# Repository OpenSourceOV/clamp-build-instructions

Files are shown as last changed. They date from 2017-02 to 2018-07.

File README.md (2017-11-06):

# Clamp Build Instructions

There are two versions of the clamp:

* [Version 2](./version-2.md) (RECOMMENDED) - complete re-design that integrates a hand lens (loupe) for magnification. This is the preferred version because of the flexibility to attach any magnification hand lens (conceivably 40x, but untested). 20x magnification is the minimum magnification for most stems.

* [Version 1](./version-1.md) - the original which uses a [Moment](https://www.shopmoment.com/) smartphone macro lens and has a magnification limit of 10x. Build instructions for Version 1 are here: [version-1.md](./version-1.md)

All clamp versions require a separate circuit to provide power and interface the Raspberry Pi with the LEDs. There are two versions. Version 1 which integrates the components on a PCB and version 2 where the components are connected inline without a PCB. Version 2 is strongly recommended unless you want to integrate other sensors, in which case Version 1 would be more useful. If you are planning to use Version 1 then you should enclose the circuit in a case.

* [Version 2](./switching-circuit-2.md) (RECOMMENDED) - inline version. Build instructions for Version 2 are here: [switching-circuit-2.md](./switching-circuit-2.md)

* [Version 1](./switching-circuit-1.md) - uses a PCB to mount the components. Build instructions for Version 1 are here: [switching-circuit-1.md](./switching-circuit-1.md)

A guide for wiring connectors is also provided:

* [Wiring Connectors](./wiring-connectors.md)

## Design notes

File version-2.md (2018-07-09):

# Clamp Version 2 Assembly Guide

## Schema

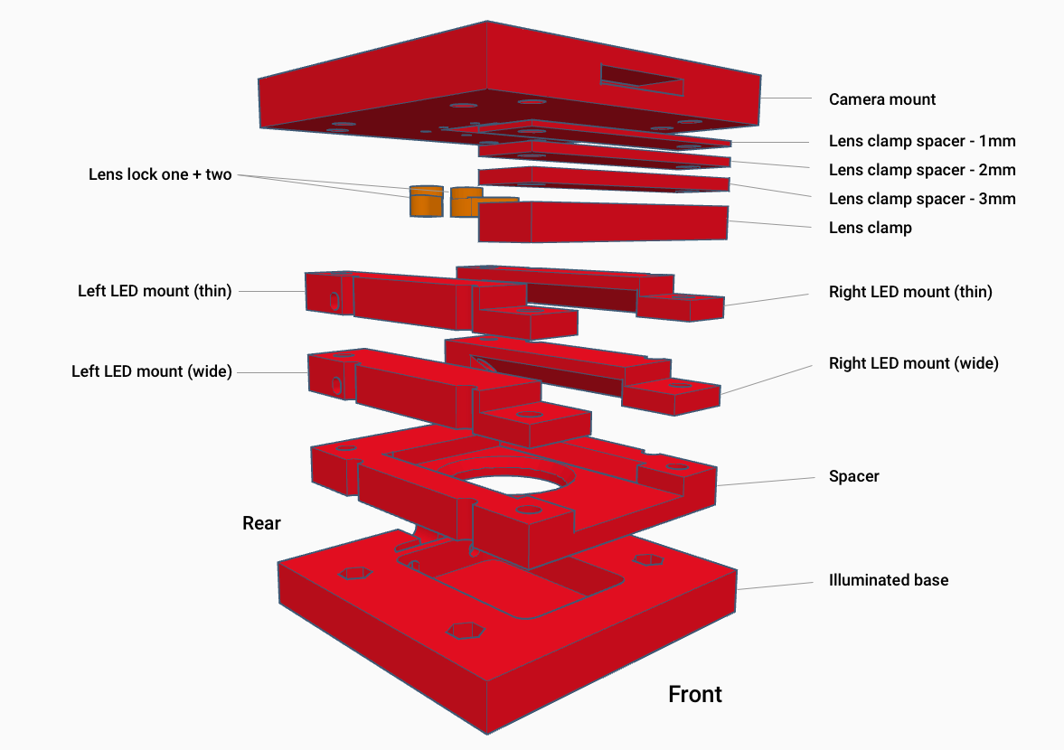
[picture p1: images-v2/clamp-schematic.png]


* **Camera mount** - to mount the camera and bolt the assembly together to the base
* **Lens clamp spacers** - used to increase the space between the top of the hand lens case and the bottom of the camera mount. Most hand lenses have a screw that sits proud and attaches the lens to the case. Without an appropriate spacer the hand lens sits at an angle. Only one need be used.
* **LED mounts** - to mount the LED strips. A wider mount to be used with most hand lenses and thinner mounts if more space is needed for a wider hand lens. Only one mount set is used (thin or wide).
* **Lens lock** - to hold the lens in place. Most lenses are firmly fixed to the case and don't move so these are normally not required.
* **Spacer** - to keep the sample in place and set the distance between hand lens and sample.
* **Illuminated base** - to provide the source of transmitted light and base for bolting the assembly together (diffuser layer not shown, more details below)

## Parts

Quantity | Part | Additional information
---------|------|---------
1|3D-printed clamp parts|Models and more information available in the [Clamp 3D Printing Resources](https://github.com/OpenSourceOV/clamp-3d-printing-resources) repository (**version 2** parts required).
6|50mm Superbright LED light strip sections|For the LED mounts and illuminated base. Usually come in long strips that can be cut into smaller sections. Typically used for accent lighting in kitchens etc. Can be purchased online from a number of places - these are some from Jaycar - [Ultra Bright IP67 Waterproof LED Flexible Strip Light](https://www.jaycar.com.au/ultra-bright-ip67-waterproof-led-flexible-strip-light/p/ZD0579). Note **50mm** sections are required.
1|Raspberry Pi Camera v2 module| See RaspberryPi.org for [more information](https://www.raspberrypi.org/products/camera-module-v2/) and list of suppliers
1|Rasberry Pi Camera long cable| Although the Camera comes with a short cable, a long cable makes life much easier. Most Raspberry Pi suppliers should stock longer cables e.g. [Little Bird Electronics - Flex Cable for Raspberry Pi Camera - 18 / 457mm](https://littlebirdelectronics.com.au/collections/raspberry-pi-cables-headers/products/flex-cable-for-raspberry-pi-camera-18-457mm)
1|Hand lens (loupe)|10-20 magnification e.g. Eschenbach 20x achromatic hand lens is excellent.
6|100mm lengths 25 AWG hookup cable (red)| For the LED mounts and illuminated base.
6|100mm lengths 25 AWG hookup cable (black)| For the LED mounts and illuminated base.
1|Sample pot of white acrylic paint| For the illuminated base.
1|Small paintbrush| For the illuminated base.
1|8mm x 90mm x 90mm (w x l x h) acrylic light diffuser (opaque plastic)|For the illuminated base.
4|5mm x ~70mm mushroom (or other) head bolts| For the illuminated base.
4|5mm x ~60mm hex head bolts| For the top assembly.
16+|5mm nuts| For the top assembly.
20+|5mm washers| For the top assembly.
4|2.5mm x 8mm screws (flat head)| For the camera mount.
4|2.5mm nuts| For the camera mount.
6|3mm nuts| For the lens locks.
2|3mm washers| For the lens locks.
2|~35mm x 3mm bolts| For the lens locks.
3|4-pin mini molex connector sets (each set containing a male and female connector)|e.g. [Jaycar - 4 Pin Mini Molex Plug/Socket](https://www.jaycar.com.au/4-pin-mini-molex-plug-socket/p/PP2027) or [Sparkfun - JST RCY Connector - Male/Female Set (2-pin)](https://www.sparkfun.com/products/10501) (but using extra to make up the connections required). For the LED mounts and illuminated base.

## Tools

Tool|Additional info|
---|-----
Soldering iron|
Solder|
Wire cutters| Flush / Diagonal cutters are particularly good e.g. [Spark fun - Flush Cutters](https://www.sparkfun.com/products/11952)
Small needle-nose pliers| e.g. [Spark fun - Needle Nose Pliers](https://www.sparkfun.com/products/8793)
Voltmeter/Multimeter| 
Third hand tool| e.g. [Spark fun - Third Hand](https://www.sparkfun.com/products/9317)

## Instructions

1. Paint the light well of the illuminated base white and leave to dry.

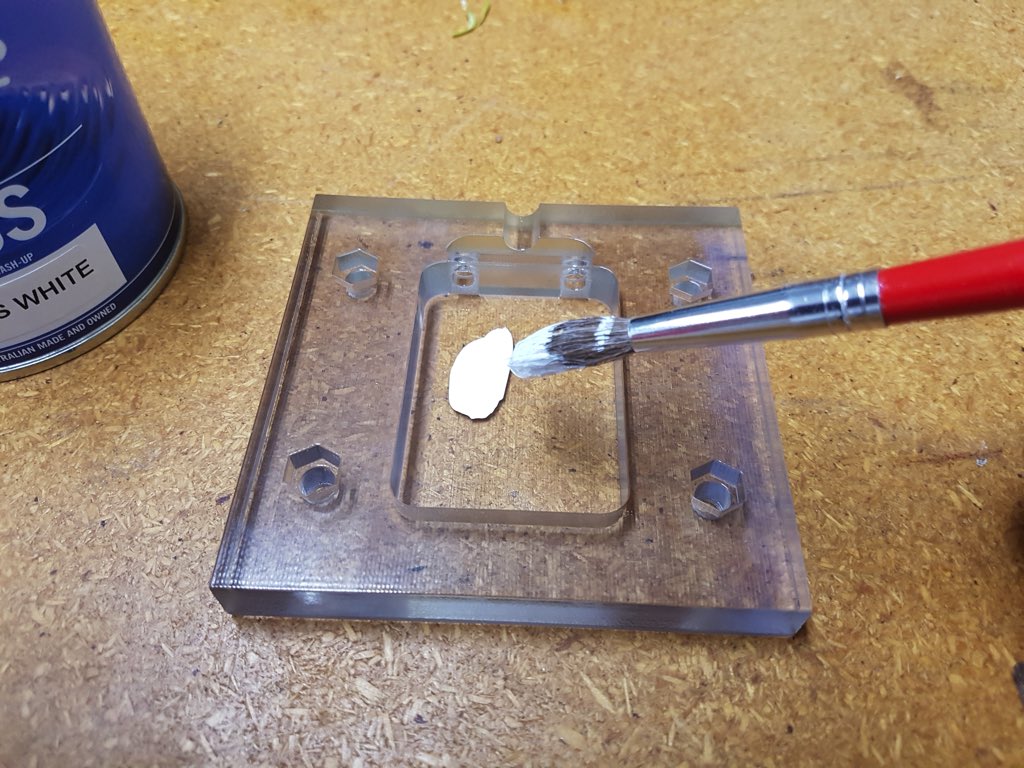
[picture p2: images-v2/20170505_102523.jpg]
    
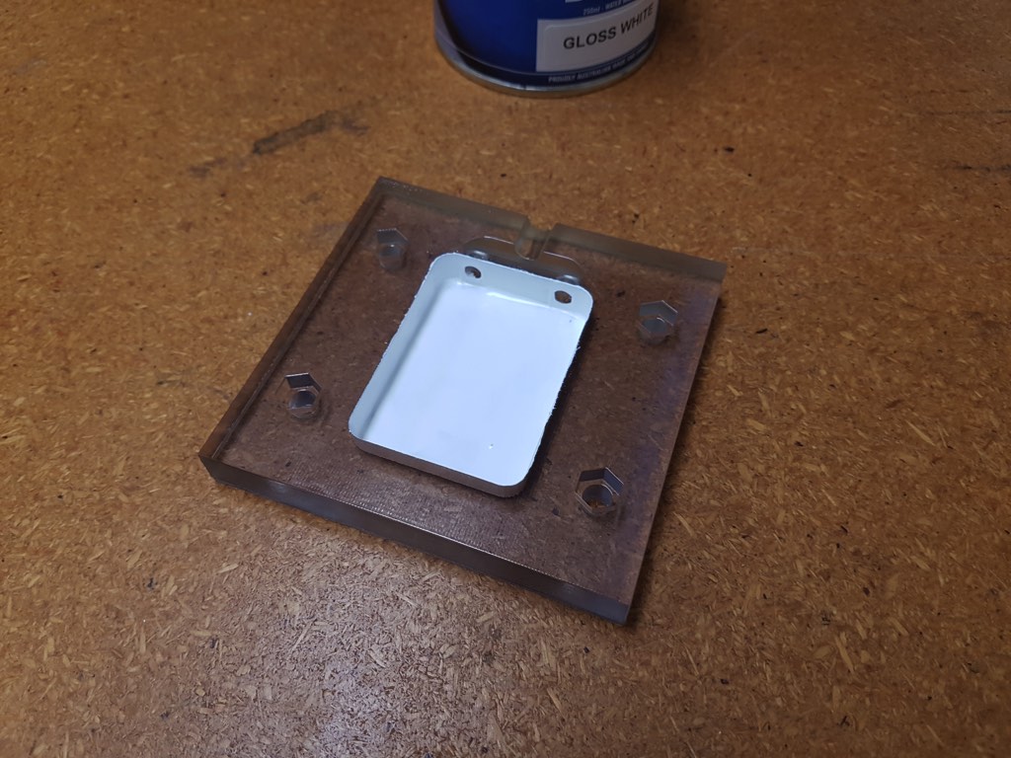
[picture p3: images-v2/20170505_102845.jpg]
    

2. Solder 100mm lengths of 25 AWG red and black wires to the positive and negative terminals of one side of each 2 50mm light strips.

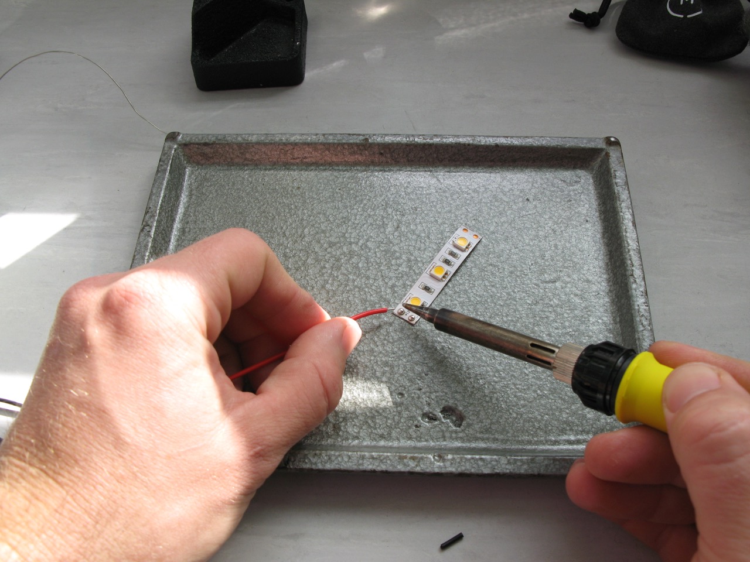
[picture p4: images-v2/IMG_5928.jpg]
    

3. Feed the wires through the holes at one end of the illuminated base, remove the adhesive backing labels and stick the LED strip sections in place as shown.

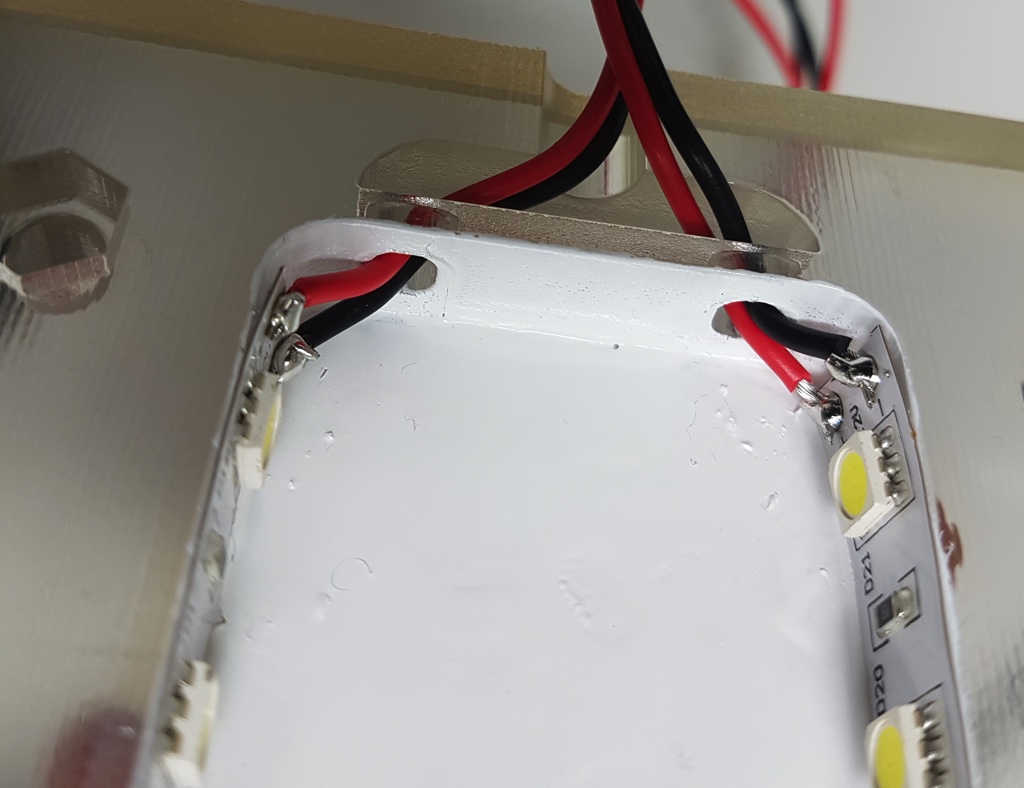
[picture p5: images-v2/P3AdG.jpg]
    

4. Insert a 5mm nut in a nut recess in the illuminated base, turn over and screw through a 5mm x ~80mm bolt. Repeat for the other 3 recesses.

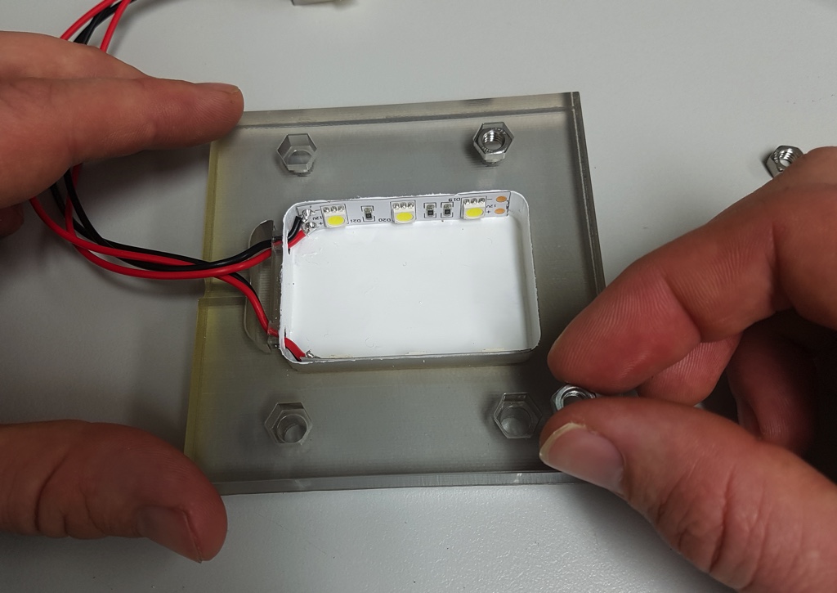
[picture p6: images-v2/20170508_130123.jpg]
    
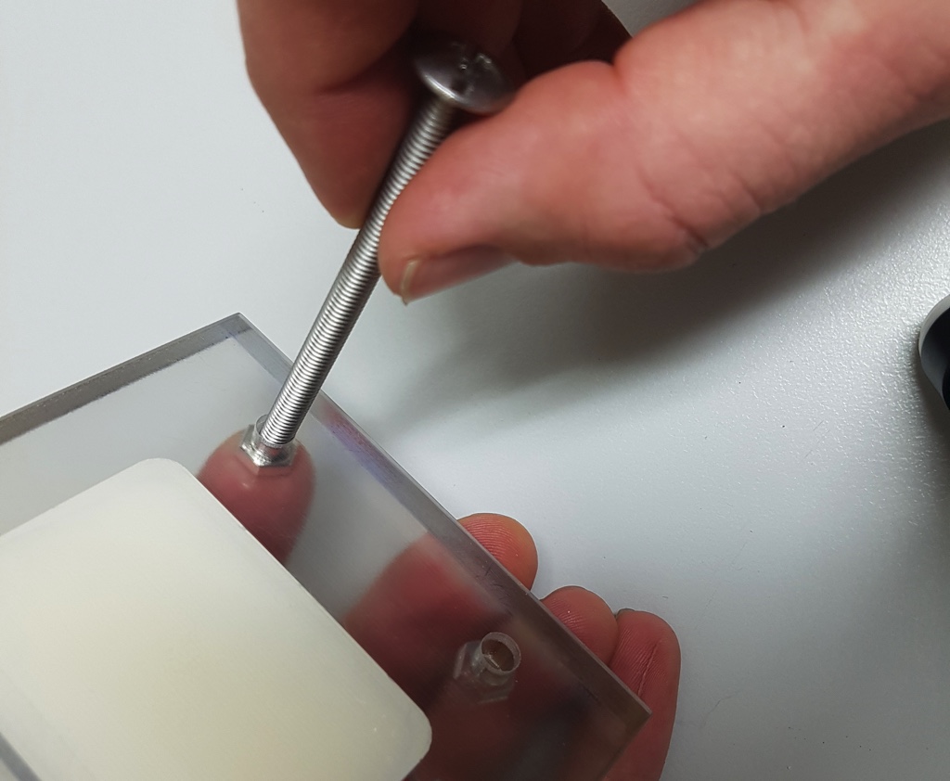
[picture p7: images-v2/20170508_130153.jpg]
    
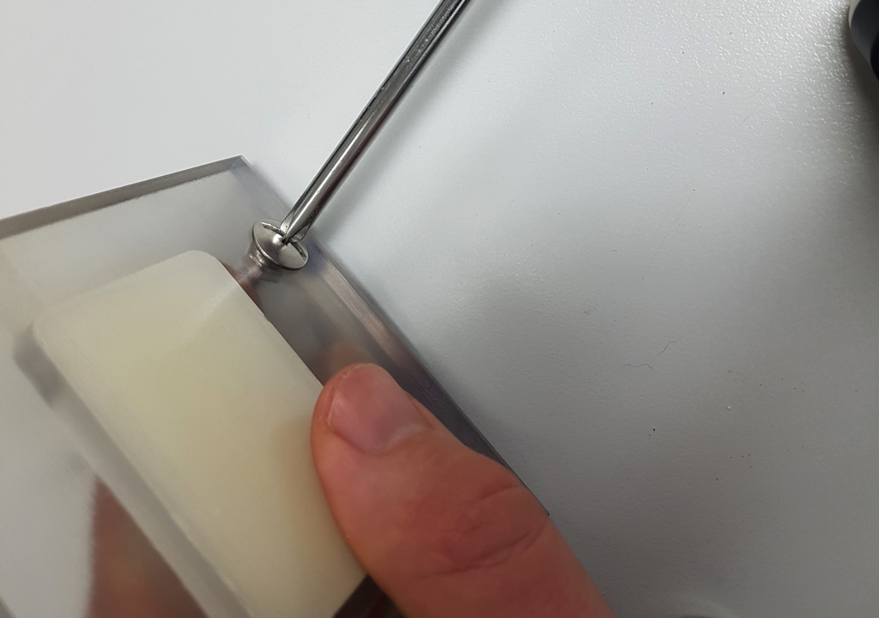
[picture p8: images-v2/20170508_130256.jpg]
    

5. Drill four holes in the diffuser and insert over the illuminator bolts. Tip: to mark where to drill the holes in the diffuser, align and hold the diffuser against the 3D printed foot then put it up against a light so you can see the holes shine through the diffuser plastic. Mark the centre of each hole with a marker then remove the diffuser, place on a flat piece of scrap wood and carefully drill through the diffuser into the wood. Gently is the key - acrylic sheets when drilled can easily shatter and crack.

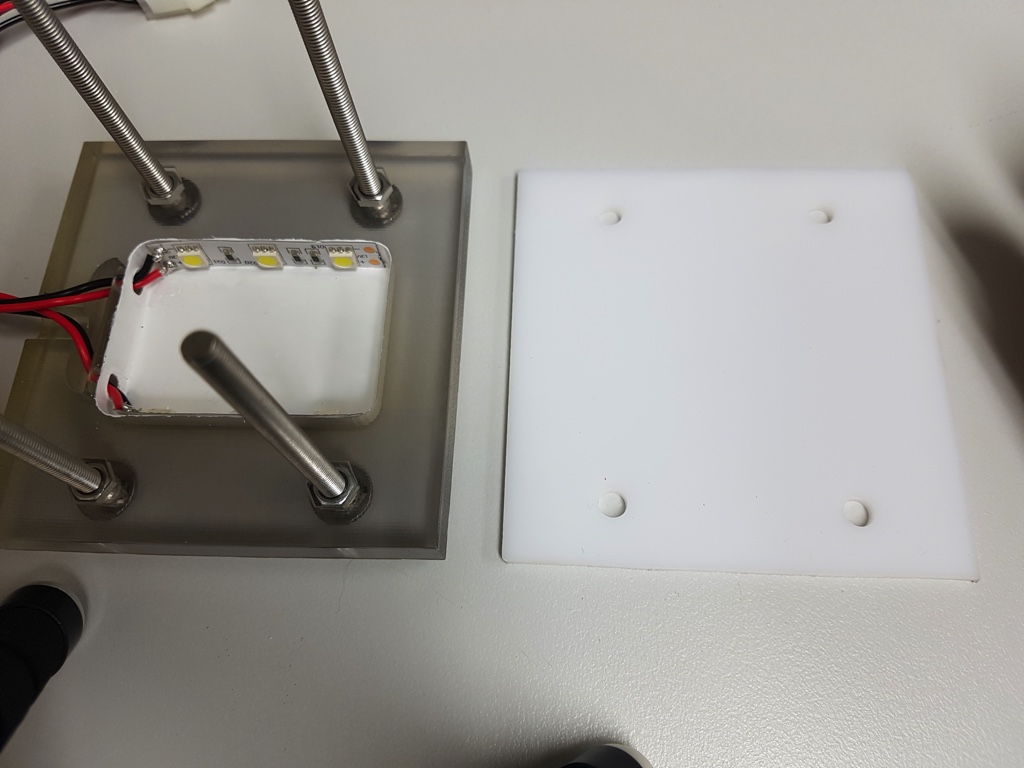
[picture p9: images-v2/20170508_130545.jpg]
    
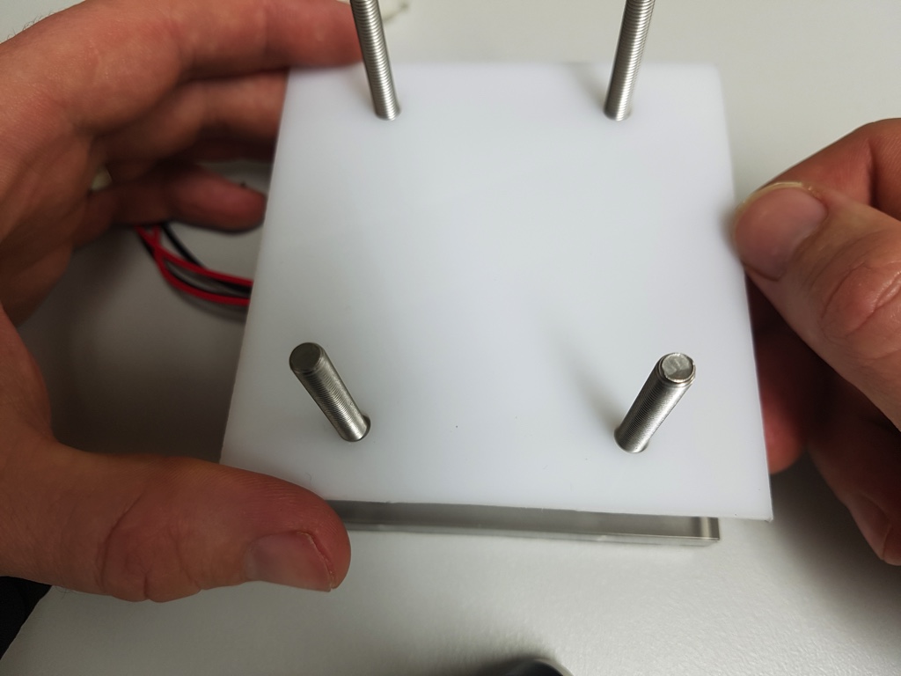
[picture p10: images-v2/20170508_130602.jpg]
    

6. Make sure the wires aren't caught between the diffuser and base, but sitting properly in the gap.

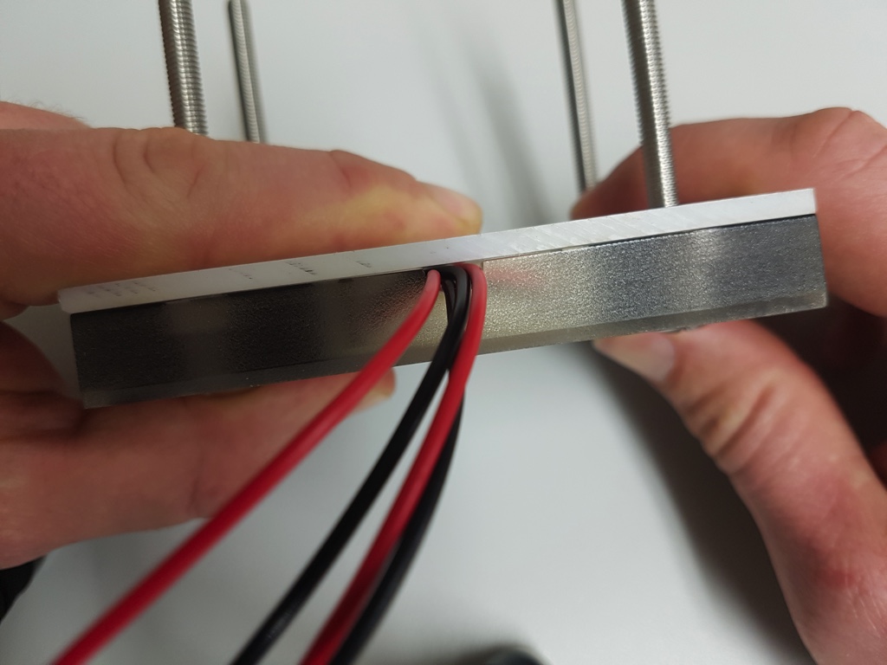
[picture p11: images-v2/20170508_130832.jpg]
    

7. Connect either male or female mini-molex connectors to the end of the wires. See [Wiring Connectors](./wiring-connectors.md) for more details.

8. Insert the spacer between the bolts and trace around the edge of the hole with a pencil or marker to provide a guide for sample positioning. Set the illuminated foot aside.

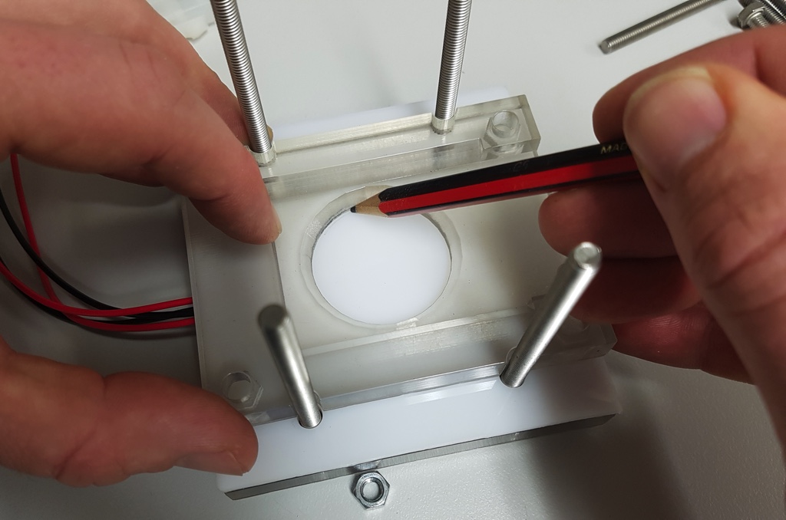
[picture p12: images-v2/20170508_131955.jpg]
    
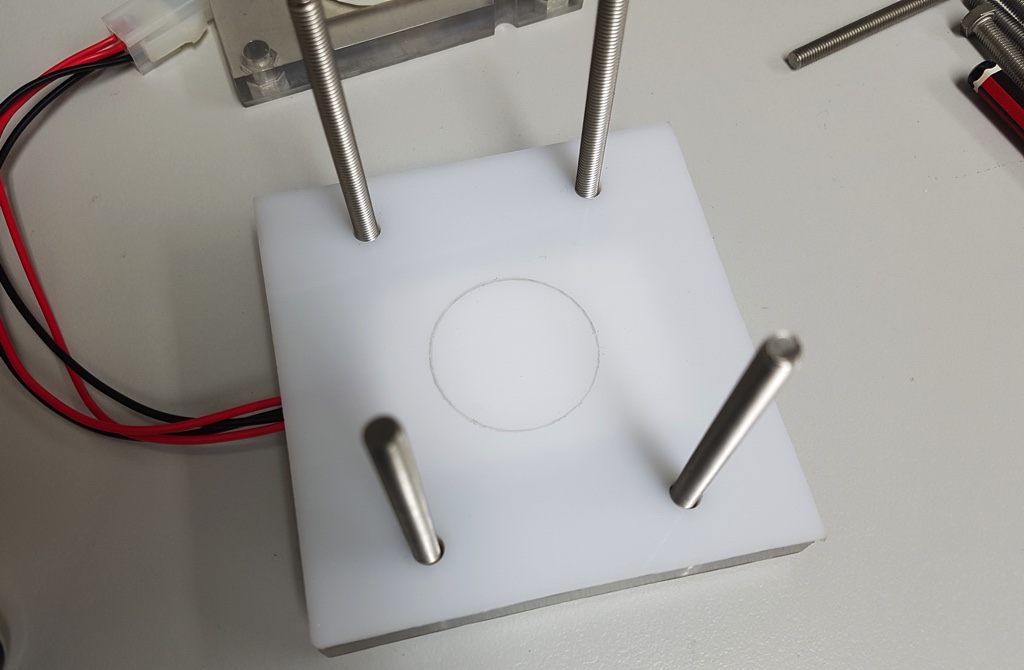
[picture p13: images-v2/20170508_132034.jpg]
    

9. Assemble the lens locks as shown.

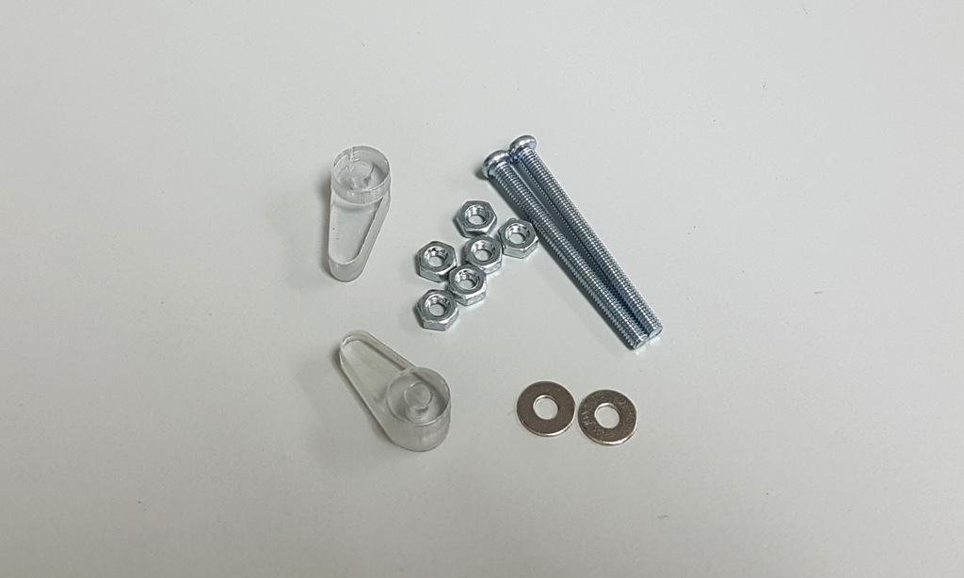
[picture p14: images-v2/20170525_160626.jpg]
    
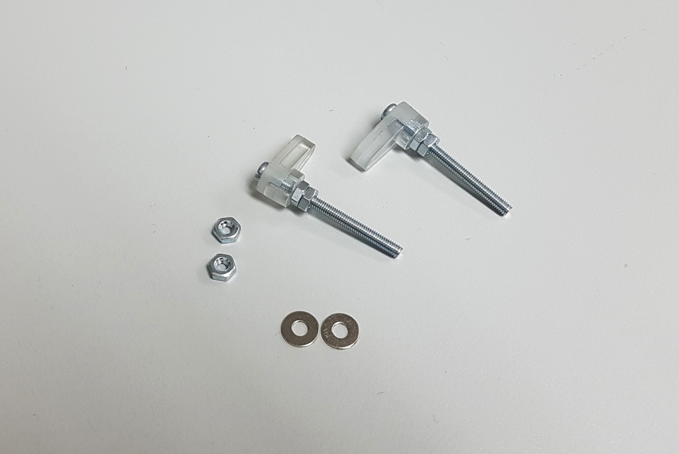
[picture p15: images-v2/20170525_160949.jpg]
    

10. Mount the Raspberry Pi camera to the camera mount (see [Version 1 instructions](./version-1.md) for more details on camera mounting) and attach the lens locks.

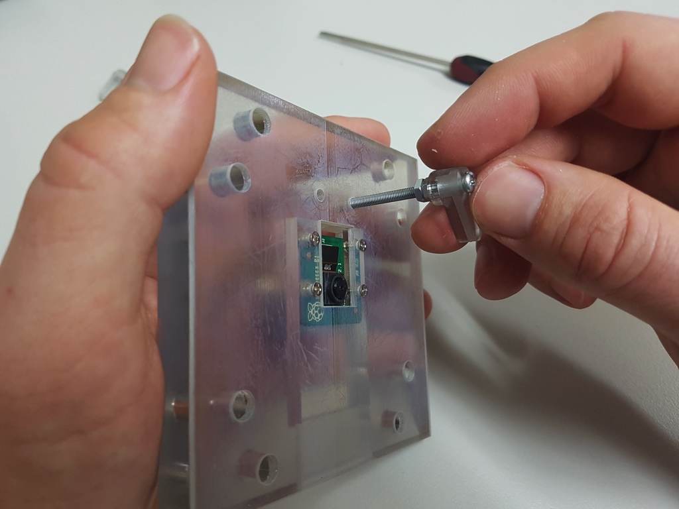
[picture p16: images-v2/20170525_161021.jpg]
    

9. Insert 4 5mm x ~60mm hex head bolts through the underside of the spacer and set the assembly flat on the bench to keep the bolts from falling out.

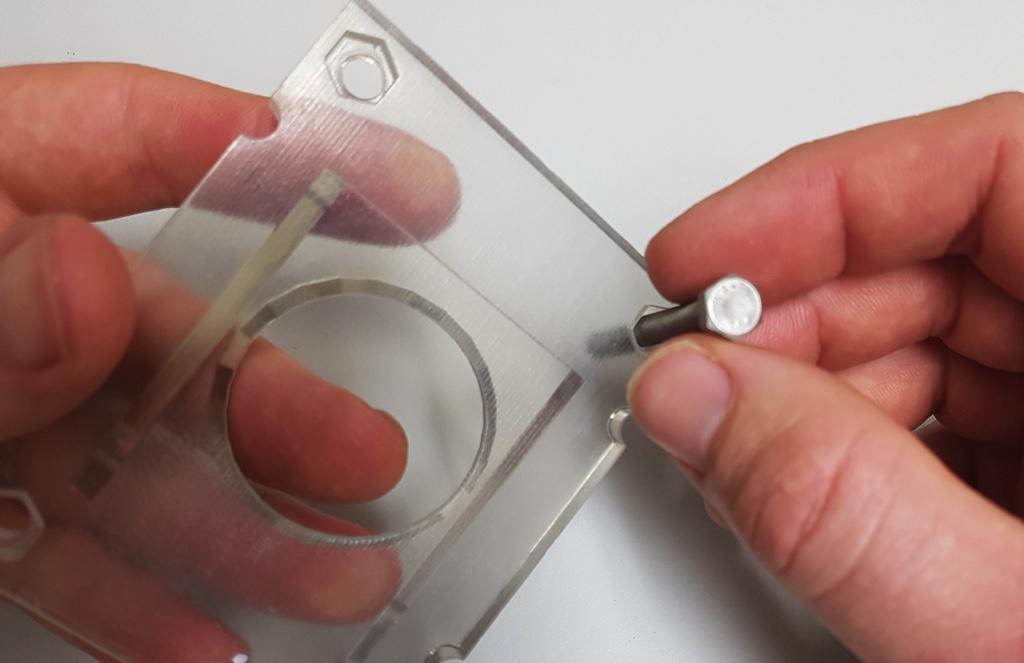
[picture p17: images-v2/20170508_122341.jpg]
    
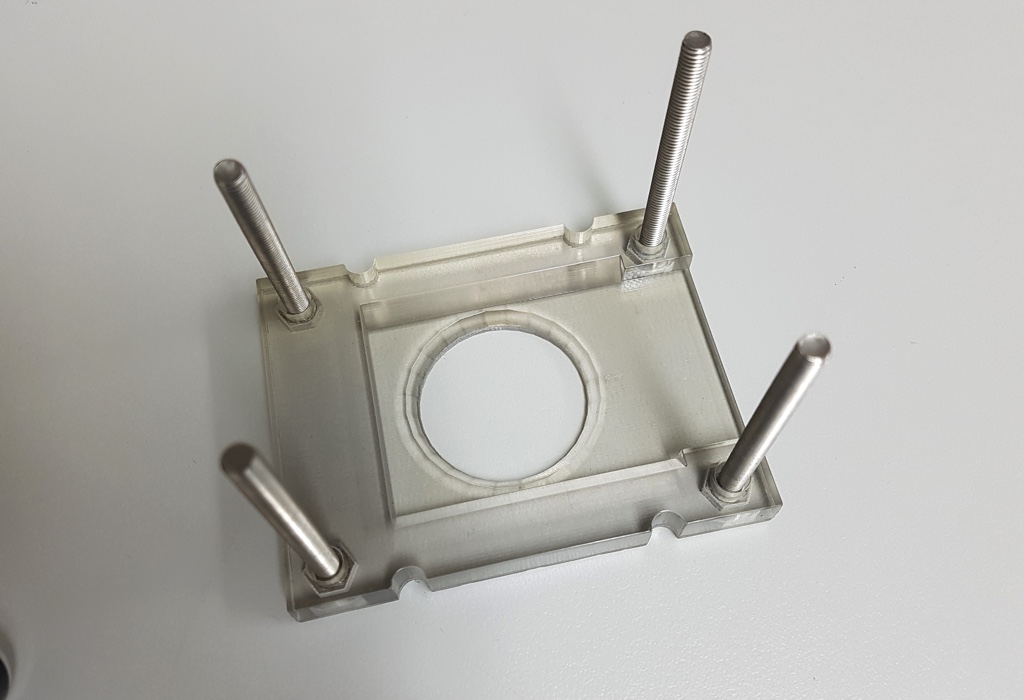
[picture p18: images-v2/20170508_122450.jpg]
    

9. Add none or 1 or 2 washers to each of the four bolts. The number of washers set the distance between the overhead illumination (the LEDs) and the sample. Whether to use none, or 1, or 2 depends on the position of the lens, which in turn depends on the lens working distance (distance between the lens and the object in focus), which will be different for each hand lens. The goal is to have the LEDs angled perfectly at the center of the spacer hole and not be obstructed by the lens. Trial and error will determine the best configuration. See [Configuration for larger working distances](#configuration-for-larger-working-distances) for an example of an alternative configuration.

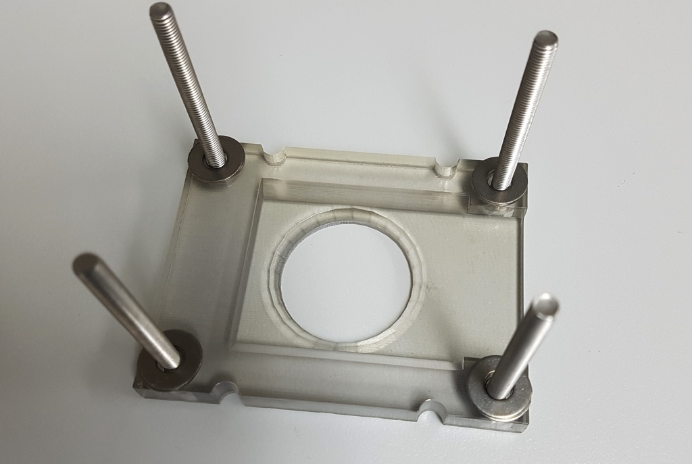
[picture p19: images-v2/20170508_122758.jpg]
    

10. Solder the LED strips and attach to the thin and wide LED mounts. Whether to use the thin or wide mounts in the final assembly depends on the hand lens. The thin LED mounts provide maximum space to accommodate a wider hand lens but comes at the cost of pushing the LEDs away from the lens and increasing the angle of reflection i.e. less direct light hitting the lens. Whether or not this makes any difference to the clarity of embolism events has yet to be tested but maximising direct light intuitively seems better, hence the wider LED mounts which position the LEDs closer to the lens.

    Solder 100mm lengths of 25 AWG red and black wires to the positive and negative terminals of one side of each 50mm light strip. Feed the wires through the holes in the LED mounts and stick the LED strips in place as shown.

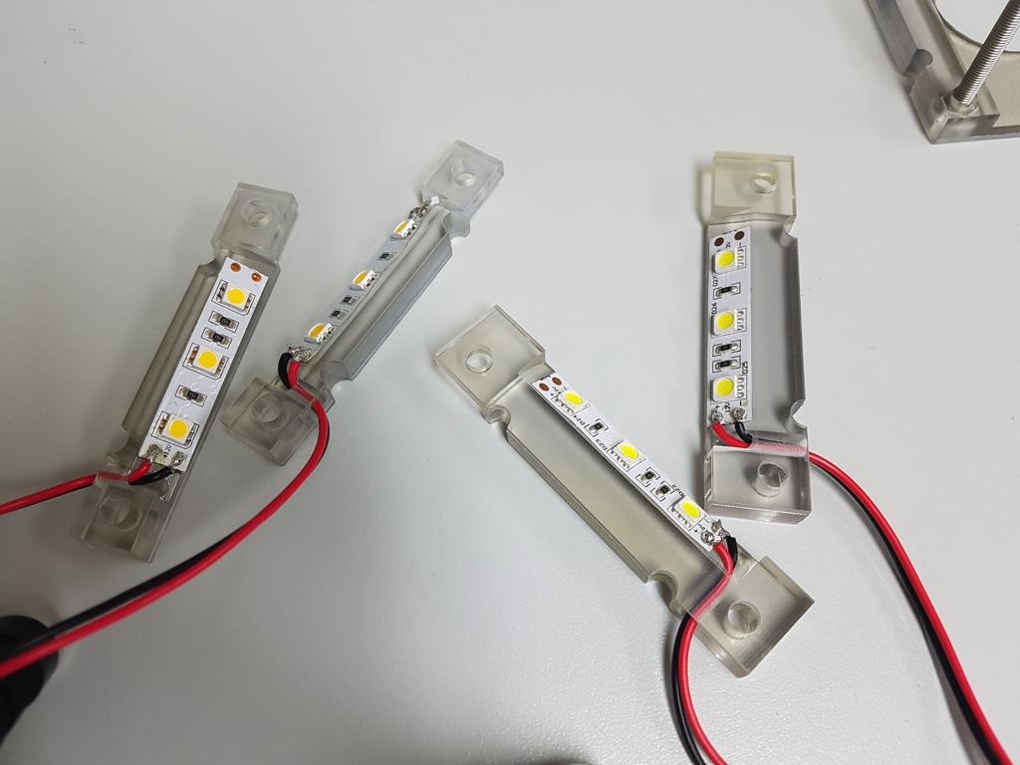
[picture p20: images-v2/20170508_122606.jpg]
    
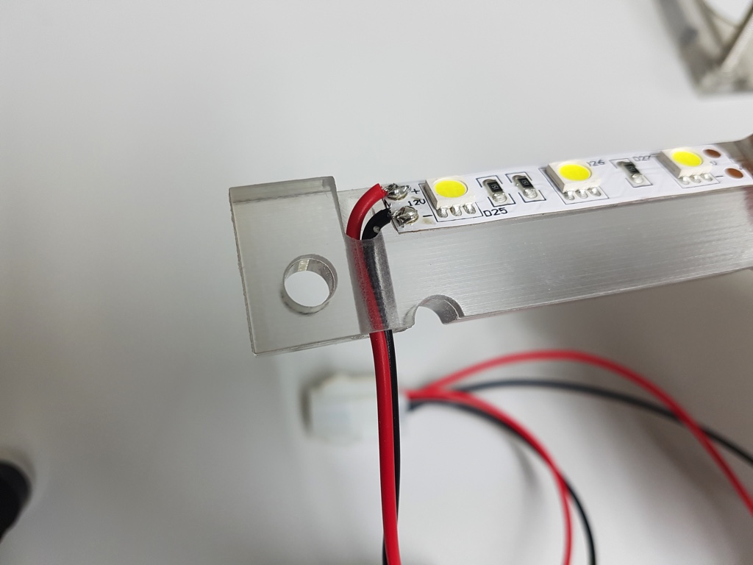
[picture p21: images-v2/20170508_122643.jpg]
    

7. Connect mini-molex connectors to the end of the wires. Use the same connector (male or female) as used for the illuminated base wires. See [Wiring Connectors](./wiring-connectors.md) for more details.

11. Add the wide or thin LED mounts to the spacer.

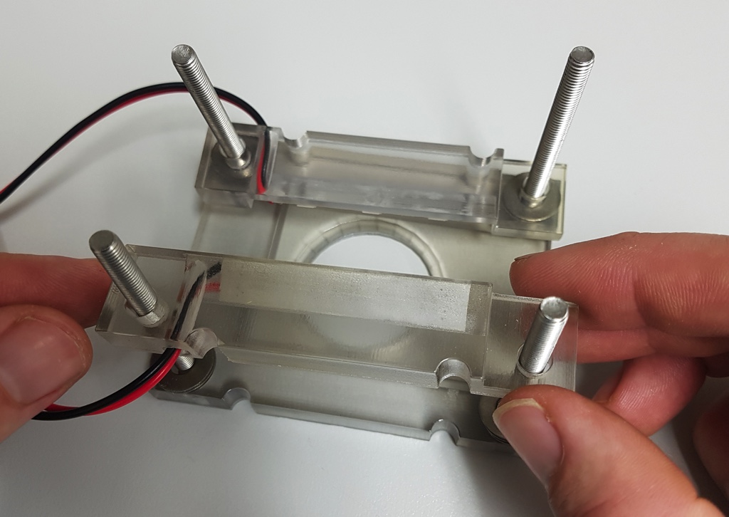
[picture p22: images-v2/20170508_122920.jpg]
    

12. Fix two 5mm nuts to the rear bolts and add two (or less/more) washers to each to act as spacers. These spacers provide support to the camera mount when bolting the assembly together. These may need to be adjusted - more detail in subsequent steps.

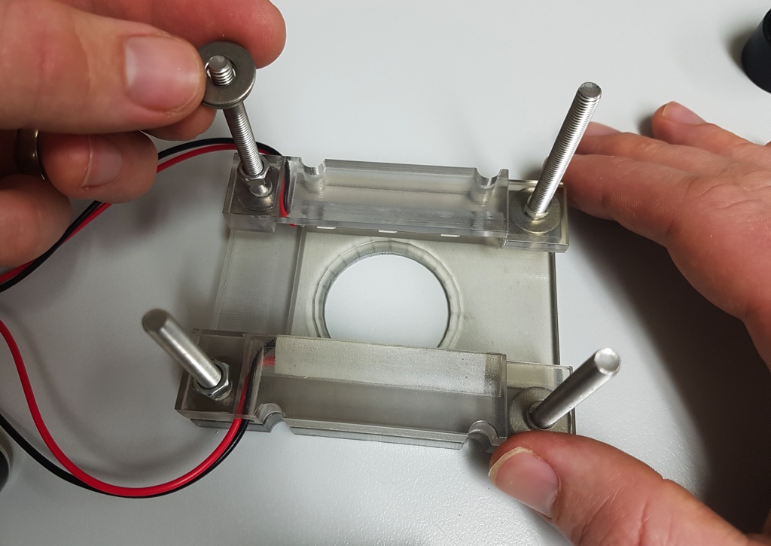
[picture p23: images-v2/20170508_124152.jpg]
    

13. Open the hand lens and insert the lens clamp through the lens housing as shown.

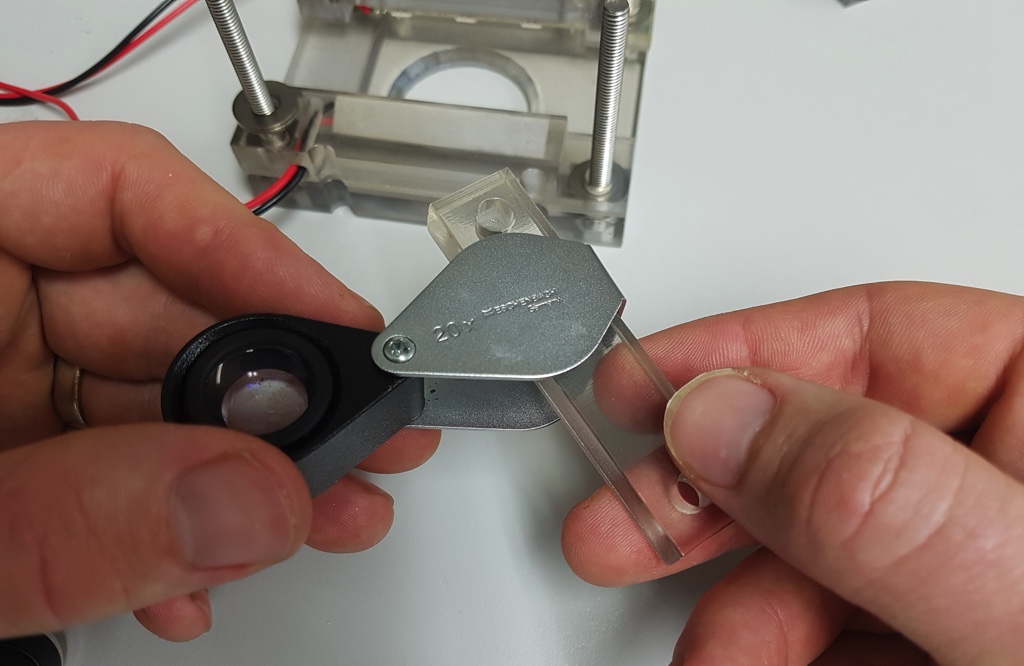
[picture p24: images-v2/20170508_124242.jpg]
    
  
14. Insert hand lens and clamp over the front bolts

    

15. Add a washer to each front bolt. These washers stop the lens clamp from bending when the assembly is tightly bolted. Ideally they should be slightly thinner than the thickness of the lens housing. If the lens housing is very thin then omit the washers completely.
    
    

16. Add a lens clamp spacer. The spacer ensures the screw that fixes the hand lens to the case doesn't touch the camera mount. For the hand lens shown the screw only sits slightly proud of the case so a 1mm spacer has been used.

    

17. Add the camera mount to the assembly. Note the hand lens will still be loose at this stage.

    

18. Add 5mm washers and bolts to the protruding bolts and **lightly tighten** - needs to be loose enough to adjust the hand lens.

    
    

19. Move the hand lens to roughly in the center (loosen the bolts if it can't be moved). The assembly should look something like this at this point:

    

20. Turn the assembly over and position the lens so the Raspberry Pi camera is in the center.

    View of the underside without the lens locks:
    

    With the lens locks:
    

21. Adjust the lens locks using a screwdriver or pencil so they touch the sides of the hand lens. 

    

21. Tighten the bolts to lock the lens case in position.

    

22. Tighten the lens lock bolts to lock the lens in position. You may need to hold the lens locks in position while tightening.

    

23. The assembly should now look something like this:

    
    
    

22. Insert the illuminated base into the top assembly and loosely attach the wing nuts (or bolts) ready for application.

    

23. Insert the Raspberry Pi camera cable through the cable gap in the mount and lock into the camera board.

    
    
    

    To detach the cable use a pair of needle-nosed/pinch pliers:

    

24. In most cases when a new sample is clamped in the device the focus will need to be micro-adjusted because the sample won't be completely flat. Adjusting the focus by adding/removing washers is a big pain (but doable if you really have to). A really simple way to add some easy additional micro-adjustment is to attach a ring of spongy material around the spacer hole. Two or three layers of neoprene (wetsuit material) works extremely well.

    (picture coming soon)

25. Done!

## Configuration for larger working distances

For hand lenses with a larger working distance, such as a 10x magnification hand lens, the space between the lens and the spacer must be increased. This can be achieved using additional bolts and washers as shown below:




Note that in these shots the two rear nuts are being moved up to meet the camera mount. This is important beacuse they provide support to the camera mount when the base is bolted to the top assembly while capturing.

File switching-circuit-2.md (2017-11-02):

# Switching/LED Circuit (Version 2 - Inline Version) Assembly Guide



## Parts

Quantity | Part | Additional information
---------|------|---------
1|60mm length 18 AWG DC power cable (black)|
1|100mm length 18 AWG DC power cable (black)| Missing from picture below
1|100mm length 18 AWG DC power cable (red)|
1|300mm length 18 AWG DC power cable (black)|
1|300mm length 18 AWG DC power cable (red)|
1|300mm length 25 AWG hookup cable (white)|
2|300mm length 25 AWG hookup cable (red)|
3|300mm length 25 AWG hookup cable (black)|
2|Jumper leads with at least one male (plug) connector (1 black, 1 white)|Can usually only buy these in packs e.g. [Spark fun - Jumper Wires Premium 6" M/F Pack of 10](https://www.sparkfun.com/products/9140)



Quantity | Part | Additional information
---------|------|---------
2|4-pin mini molex connector sets (each set containing a male and female connector)|e.g. [Jaycar - 4 Pin Mini Molex Plug/Socket](https://www.jaycar.com.au/4-pin-mini-molex-plug-socket/p/PP2027) or [Sparkfun - JST RCY Connector - Male/Female Set (2-pin)](https://www.sparkfun.com/products/10501) (but using 1 extra to make up the four connections required).
1|2-pin molex connector set (with both male and female connector)|e.g. [Jaycar - 2 Pin MULTI Pin Plug / Socket](https://www.jaycar.com.au/2-pin-multi-pin-plug-socket/p/PP2020)
1|TIP122 NPN transistor| e.g. [Jaycar - TIP122 NPN Transistor](https://www.jaycar.com.au/tip122-npn-transistor/p/ZT2292). Datasheet available here - [TIP122-datasheet](./resources/TIP122-datasheet.pdf).
2|Large alligator clips (1 red 1 black)|e.g. [Jaycar - Alligator Clips](https://www.jaycar.com.au/alligator-clips-with-screw-pk-2/p/HM3025).
-|Multiple lengths of difference sized heatshrink| Available in kits (e.g. [Sparkfun - Heat Shrink Kit](https://www.sparkfun.com/products/9353)) but often cheaper to buy in long strips and cut yourself.



## Tools

Tool|Additional info|
---|-----
Soldering iron|
Solder|
Wire cutters| Flush / Diagonal cutters are particularly good e.g. [Spark fun - Flush Cutters](https://www.sparkfun.com/products/11952)
Small needle-nose pliers| e.g. [Spark fun - Needle Nose Pliers](https://www.sparkfun.com/products/8793)
Voltmeter| 
Third hand tool| e.g. [Spark fun - Third Hand](https://www.sparkfun.com/products/9317)
Heatgun or lighter| Used to heat the heatshrink.

## Instructions

1. Strip ~4mm of insulation from one end of the red and black 100mm length 18 AWG DC power cables and solder the 2-pin molex pins, one for each wire.

    
    
    
    
    
    

    See the [Wiring Connectors Guide](./wiring-connectors.md) for additional information.

2. Splay the pins of the TIP122 transistor.

    
    

3. Strip ~10mm of insulation from one end of the white hookup cable, twist then wrap around pin 1 (base) - the leftmost pin when viewing the TIP122 transistor from the front. See the [TIP122 datasheet](./resources/TIP122-datasheet.pdf) for more information.

    

4. Support the transistor and solder the cable to the pin. The trick here is not to heat the pin (and transistor) for too long but a good soldered connection is still required.

    
    

5. Strip ~10mm of insulation from one end of the two 100mm lengths of black hookup cable. Twist the ends then wrap each cable around the middle pin (collector) and solder.
    
    
    
    

6. Strip ~10mm of insulation from the one end of the black 60mm black power cable and wrap around the remaining pin (emitter). Solder.
    
    
    
    

7. Using wire-cutters remove any excess wires and generally clean up the pins

  (pictured required)

8. Add appropriate heatshrink sections, apply heat, and push the pins back together (from their splayed positions). Try and get the heatshrink as high up the pins as possible so the entire pin is insulated.

    
    

9. Align the transistor assembly with the power cable assembly so there is a gap of ~50mm between the transistor and the molex connector. Cut the black earth cable from the molex connector and the black cable connected to the emitter (pin 3) and remove ~15mm of insulation. 

    
    
    
10. Remove ~15mm from the remaining 300mm length of black hookup cable. Twist and wrap the hookup and power cable as shown and solder. Soldering a large bundle of wires like this can be tricky. You need to get enough heat into the cable for the solder to flow so you need a clean soldering iron tip that is properly tinned to maximise heat transfer. If you can't get a good connection with solder then use some wire connectors. Add heatshrink to insulate.

    
    
    
    

11. Remove ~15mm insulation from the two remaining 300mm lengths of red hookup cable and the end of the red power cable coming from the molex connector. Twist as shown and solder. Apply heatshrink.

    
    
    
    

12. At this point you should have something that looks like this:

    

13. Strip ~4mm from the ends of all of the hookup cables (not the power cables) EXCEPT the hookup cable connected to pin 3 (emitter) of the transistor.

    

14. Attach and solder a molex pin from the male or female 4-pin molex connector. Don't insert into the molex connector just yet. 

    
    
    

15. Measure up an appropriate length of large heatshrink to cover the bulk of the transistor and wires (~100-150mm section). Cut, insert the wires, and heat shrink.

    
    
    

16. Insert the 4 wires with the molex pins into another length of appropriately sized heatshrink (~100mm).

    

17. Now insert the pins into the 4-pin molex connector and heat shrink.

    

18. Cut the two jumper leads at the female end leaving ~ 15mm of wire. Strip ~8-10mm of insulation from the ends.

    
    
    

19. You should now have two hookup wires (the thinner wires) remaining - a white wire coming from the transistor and a black wire coming from the molex connector. Insert the wires through two ~20mm lengths of heatshrink - one black and one white if you can to match the wire colours.

    

20. Strip ~10mm insulation from the ends and attach the jumper leads by twisting the wires together. Move the heatshrink as far away from the twisted wires as possible then solder. If the heatshrink is too close it will shrink when you solder! Once soldered move the heatshrink back up and over the connection and heat shrink.

    
    
    
    

21. At this point you should have something that looks like this:

    

22. Now to construct the power leads:

    

23. Strip ~5mm of insulation from the ends of the two remainin 300mm lengths of power cable (black and red).

    

24. Attach the pins for the male/female (depends what you used in step 1) 2-pin molex connector

    

25. Insert the pins into the 2-pin molex connector. Tip: insert the connector part way into its mating connector (as you can see in the pic) and then insert the pins. This way you can make absolutely sure that you are meeting red with red and black with black. Once the molex connectors are in they are near impossible to get out without a special tool (and even then you'll probably damage the pins).

    

26. Strip ~15mm from the other end of the power cable, twist, and thread through the clip cap/sleeve as shown. Bend ~4mm of the end to help you fit the wire into the clip.

    

27. Thread the cable through the clip hole (this will be easier with the ~4mm bend) and wrap around the screw and tighten.
    
    

28. Apply some solder to the cable and clip to ensure a good connection. Only a little blob of solder on one side is needed.
    
    

29. Repeat for the other power cable. Bring up and fix the clip caps/sleeves.

30. Done! Go get a beer and marvel at your work.



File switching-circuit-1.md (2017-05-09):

# Switching/LED Circuit Assembly Guide

## Parts

Quantity | Part | Additional information
---------|------|---------
4|100mm lengths 25 AWG hookup cable (red)|
4|100mm lengths 25 AWG hookup cable (black)|
2|4-pin mini molex connector sets (each set containing a male and female connector)|e.g. [Jaycar - 4 Pin Mini Molex Plug/Socket](https://www.jaycar.com.au/4-pin-mini-molex-plug-socket/p/PP2027) or [Sparkfun - JST RCY Connector - Male/Female Set (2-pin)](https://www.sparkfun.com/products/10501) (but using 1 extra to make up the four connections required).
1|2-pin molex connector set (with both male and female connector)|e.g. [Jaycar - 2 Pin MULTI Pin Plug / Socket](https://www.jaycar.com.au/2-pin-multi-pin-plug-socket/p/PP2020)
1|TIP122 NPN transistor| e.g. [Jaycar - TIP122 NPN Transistor](https://www.jaycar.com.au/tip122-npn-transistor/p/ZT2292). Datasheet available here - [TIP122-datasheet](./resources/TIP122-datasheet.pdf).
1|100mm length 25 AWG hookup cable (white)
3|100mm length 25 AWG hookup cable (black)
2|100mm length 25 AWG hookup cable (red)
1|100mm length 18 AWG DC power cable (red)
1|100mm length 18 AWG DC power cable (black)
1|100m+ length 18 AWG DC power cable (red)
1|1000+ length 18 AWG DC power cable (black)
1|2-way PCB mount screw terminal| e.g [Sparkfun - Screw Terminals 2.54mm Pitch (2-Pin)](https://www.sparkfun.com/products/10571)
1|PCB|"Links" and "Strips" version is being used here e.g. [Little Bird - Ultra Mini Experimenters Board](https://littlebirdelectronics.com.au/products/ultra-mini-experimenters-board)
2|Jumper leads with at least one male (plug) connector (1 black, 1 white)|Can usually only buy these in packs e.g. [Spark fun - Jumper Wires Premium 6" M/F Pack of 10](https://www.sparkfun.com/products/9140)
2|~20mm sections of heatshrink tubing (~3mm diameter)|Usually purchased in longer lengths or in packs e.g. [Spark fun - Heat Shrink Kit](https://www.sparkfun.com/products/9353)

## Tools

Tool|Additional info|
---|-----
Soldering iron|
Solder|
Wire cutters| Flush / Diagonal cutters are particularly good e.g. [Spark fun - Flush Cutters](https://www.sparkfun.com/products/11952)
Small needle-nose pliers| e.g. [Spark fun - Needle Nose Pliers](https://www.sparkfun.com/products/8793)
Voltmeter| 
Third hand tool| e.g. [Spark fun - Third Hand](https://www.sparkfun.com/products/9317)

## Instructions



For this particular version we have used a PCB with "links" and "strips" which takes care of the connections between the parts. There are many alternatives and the easiest would be to use a solderless [breadboard](https://www.sparkfun.com/products/12002), which does not require any soldering. However these are only good for prototyping and unsuitable for every day use because the parts and wires can easily pull out of the sockets. A number of good online guides for soldering are provided at [http://www.opensourceov.org/resources/](http://www.opensourceov.org/resources/).

This guide assumes you're building the circuit using the links and strips PCB. Use the following image as a reference for the wires and connection points.



1. Attach all the parts to the board except for the hookup cables. Bend the wires outward so the parts stay in their holes while soldering.

    

2. Solder all the connections.

    

3. Trim the ends.

    

4. Strip around 8mm of insulation from the end of the wires that connect from the Pi to the board and the board to the two LED strips (6 wires in total, only 4 shown) and twist the ends so they are easy to insert into the PCB holes.

    

5. Insert into the appropriate holes, bend outwards and solder.

    
    

6. Attach and solder the PCB mount screw terminal.

    

7. Strip about 10mm of insulation from the unstripped ends of the black and white wires that connect to the Pi and twist the exposed wire. Add the two sections of heatshrink (don't apply heat yet).

    
    

8. Remove one end of each of the two jumper leads leaving a female socket connector at one end of each (these will connect to the Pi GPIO pins). Strip about 10mm of insulation from the end.

    

9. Join the black and white jumper leads to the black and white hookup cable by twisting the wires around each other.

    

10. Suspend the wire connection using a third hand tool.

    

11. Apply some solder to the tip of a hot soldering iron and place it under the wound wires so the solder is touching the wires. Now move the hot iron back and forth along the wound wires while adding more solder to the top. This will thoroughly coat the wires and ensure a good connection.

    

12. Move the heatshrink over the soldered connection and heat to shrink.

    
    

13. Repeat for the other wire.

    

14. Attach the four wires (2 red, 2 black) that will connect to the LEDs to the unused female (or male) 4-pin mini-molex connector, following the same procedure as before. Make sure the terminals are matching (red to red, black to black) before you push the pins into their housing.

    
    

15. Strip 3-4mm of insulation from two of the 18 AWG wires (1 black, 1 red). These will be used to connect the power supply.

    

16. Install the male 2-pin molex connector. Same procedure as the 4-pin mini molex connector. With the larger molex connector it may be easier to crimp the two flaps of metal that hold the insulation in place (as shown here).

    
    
    
    

17. Strip 3-4mm of insulation from the other end of the two wires and insert into the PCB mount screw terminalensuring that the black wire is connected to the negative terminal and the red wire to the positive terminal as shown in the reference diagram above. 

    
    

17. Install the female connector on a second set of 18 AWG wires (1 red, 1 black). These wires can then be attached to a 12v battery.

    
    

18. Done!



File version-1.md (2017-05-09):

# Clamp Version 1 Assembly Guide

## Parts

Quantity | Part | Additional information
---------|------|---------
1|3D-printed clamp housing parts (4 parts in total)|Models and more information available in the [Clamp 3D Printing Resources](https://github.com/OpenSourceOV/clamp-3d-printing-resources) repository.
1|3D-printed illumination foot|Models and more information available in the [Clamp 3D Printing Resources](https://github.com/OpenSourceOV/clamp-3d-printing-resources) repository
4|50mm Superbright LED light strip sections|Usually come in long strips that can be cut into smaller sections. Typically used for accent lighting in kitchens etc. Can be purchased online from a number of places - these are some from Jaycar - [Ultra Bright IP67 Waterproof LED Flexible Strip Light](https://www.jaycar.com.au/ultra-bright-ip67-waterproof-led-flexible-strip-light/p/ZD0579). Note **50mm** sections are required.
1|Raspberry Pi Camera v2 module| See RaspberryPi.org for [more information](https://www.raspberrypi.org/products/camera-module-v2/) and list of suppliers
1|Rasberry Pi Camera long cable| Although the Camera comes with a short cable, a long cable makes life much easier. Most Raspberry Pi suppliers should stock longer cables e.g. [Little Bird Electronics - Flex Cable for Raspberry Pi Camera - 18 / 457mm](https://littlebirdelectronics.com.au/collections/raspberry-pi-cables-headers/products/flex-cable-for-raspberry-pi-camera-18-457mm)
1|Moment 10x macro lens| Available from [Moment](https://momentlens.co/).
4|100mm lengths 25 AWG hookup cable (red)|
4|100mm lengths 25 AWG hookup cable (black)|
4|2.5mm x 8mm screws (flat head) and nuts|
4|3mm nuts|
4|3mm x ~35mm bolts|
4|5mm x ~75mm hex head bolts|
9|5mm nuts|
1|Sample pot of white acrylic paint|
1|Fine paintbrush|
4|5mm x ~80mm hex head bolts|
1|8mm x 90mm x 60mm (w x l x h) acrylic light diffuser (opaque plastic)
2|4-pin mini molex connector sets (each set containing a male and female connector)|e.g. [Jaycar - 4 Pin Mini Molex Plug/Socket](https://www.jaycar.com.au/4-pin-mini-molex-plug-socket/p/PP2027) or [Sparkfun - JST RCY Connector - Male/Female Set (2-pin)](https://www.sparkfun.com/products/10501) (but using 1 extra to make up the four connections required).

## Tools

Tool|Additional info|
---|-----
Soldering iron|
Solder|
Wire cutters| Flush / Diagonal cutters are particularly good e.g. [Spark fun - Flush Cutters](https://www.sparkfun.com/products/11952)
Small needle-nose pliers| e.g. [Spark fun - Needle Nose Pliers](https://www.sparkfun.com/products/8793)
Voltmeter/Multimeter| 
Third hand tool| e.g. [Spark fun - Third Hand](https://www.sparkfun.com/products/9317)

## Instructions

The 3D printed clamp housing consists of four parts:

* Camera mount
* Lens housing
* LED housing
* Spacer



1.  Solder 100mm lengths of 25 AWG red and black wires to the positive and negative terminals of one side of each 50mm light strip. Put two of the LED strips aside for later (to be used for the illumination foot)

    
    

2.  For each LED strip section feed the wires through the hole, remove the adhesive backing label and stick the LED strip section in place.

    
    
    

3. Mount the camera using the four 8mm screws and nuts. Insert the screws from underneath to ensure there is enough clearance between the screws and the macro lens.

    
    
    
    
    

4. Insert four 3mm nuts into the four nut recesses in the LED housing

    

5. Insert the Moment macro lens into the lens recess in the LED housing

    

6. Hold the LED wires in place in the LED wires channel and add the lens housing ensuring that the two parts are joined flush.

    
    
    

7. Add the camera mount to the top. The camera lens sits slightly proud of the mount and should slot into the opening of the macro lens. Take special care to ensure the two are aligned. Turn the assembly over and look through the macro lens to check that the camera and lens are aligned. 

    Depending on the quality and accuracy of the 3D printer you may need to adjust one or more of the holes that mount the camera until the lens and camera are correctly aligned. A dissecting microscope can be helpful in ensuring alignment.

    

8. Screw the assembly together using the four 3mm x ~35mm bolts which will screw into the nuts inset in the LED housing. This should be done slowly and carefully to ensure that the camera is not forced into the top of the lens.

    
    

9. Attach the four 5mm x ~75mm bolts to the spacer through the underside and fix with four 5mm nuts on the top.

    
    
    

10. Screw on four additional 5mm nuts to be used as spacers.

    

11. Insert spacer into the main assembly.

    
    

12. Attach with a single 5mm nut.

    

13. Paint the inside of the illumination foot and attach the two remaining LED strips to two of the faces and feed the wires through the holes. Note the image shows the light foot printed with a transparent plastic. Transparent material is not required. The most important thing is that the light well is painted with a reflective material such as white paint (acrylic-based works well).

    

14. Insert the four 5mm x ~80mm bolts through the underside of the illumination foot.

    

15. Drill four holes in the diffuser, insert over the bolts and fix with four 5mm nuts. Tip: to mark where to drill the holes in the diffuser, align and hold the diffuser against the 3D printed foot then put it up against a light so you can see the holes shine through the diffuser plastic. Mark the centre of each hole with a marker then remove the diffuser, place on a flat piece of scrap wood and carefully drill through the diffuser into the wood. Gently is the key - acrylic sheets when drilled can easily shatter and crack.

    
    

16. Insert light box into main assembly.

    
    

17. Insert the camera cable.

    

### Wiring up the connectors

See [Wiring Connectors](./wiring-connectors.md) for instructions.

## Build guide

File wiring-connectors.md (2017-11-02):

### Wiring Connectors

We have suggested to use 4-pin mini molex connectors to connect the lights to the light switching circuit and 2-pin molex (size up from mini) connectors to connect the light switching circuit to a 12v power supply. This makes connecting/reconnecting the lights and power supply easy and reduces the chance that a user will connect the terminals incorrectly (the connectors can only be inserted one way). However, they can be tricky to install (common problems are listed at step 7). There are endless [other connectors](https://www.sparkfun.com/categories/91) if alternatives are needed/preferred.

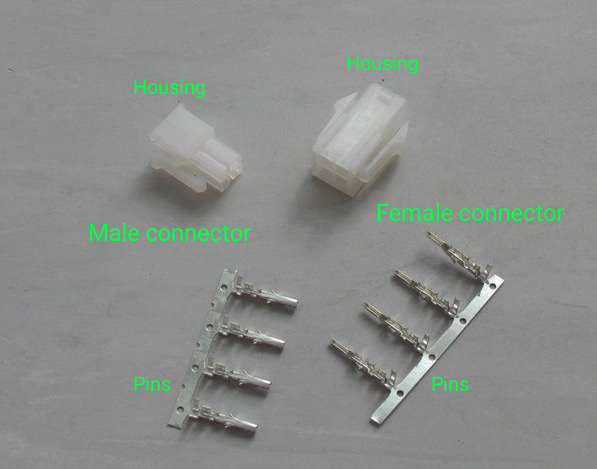
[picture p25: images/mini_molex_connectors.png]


1. Strip the ends of the eight LED wires (4 from the LED housing and 4 from the illumination foot) leaving around 4mm of exposed wire. Only four of the eight wires are shown in the picture.

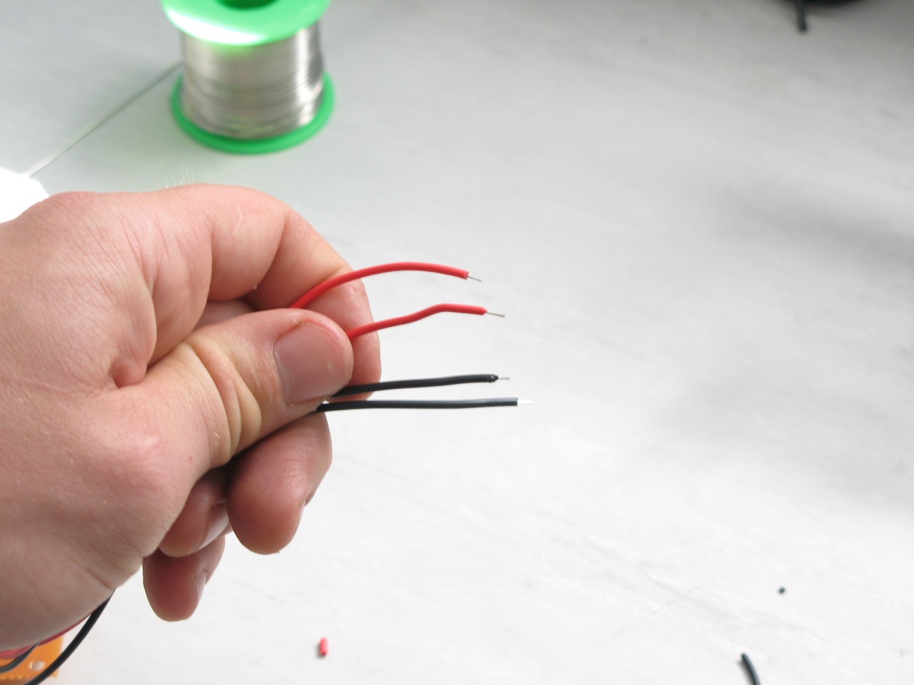
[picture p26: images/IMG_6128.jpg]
    

2. You can attach the wire to the pins using a crimping tool but a soldered connection is better. Do one pin at a time. Insert the wire part way into the pin as shown below and use a third hand clip to secure the wire to the pin while soldering.

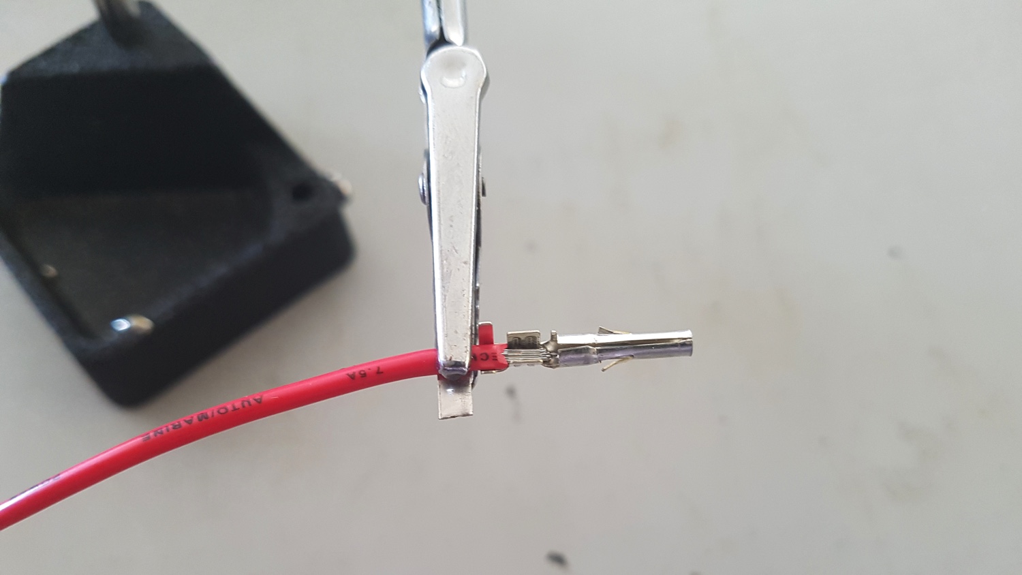
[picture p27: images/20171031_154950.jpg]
    
    
3. Add a small amount of solder to the tip of the soldering iron then push the tip into the pin so the solder touches the exposed wire (which is touching the pin). Leave for a brief moment so the iron (via the little bit of solder) heats the wires and pin. Now add more solder. The solder should flow in and around the wires. As soon as it does the remove the soldering iron. If the pin gets too hot then the wire insulation will melt, so the trick is to have the soldering iron heating the pin long enough so enough solder is added ensuring a good connection but not so long that the wire insulation melts and becomes a mess (it always melts a little). Make sure the solder stays within the pin channel. If you're having problems later inserting the pin into housing then this could be the problem. 

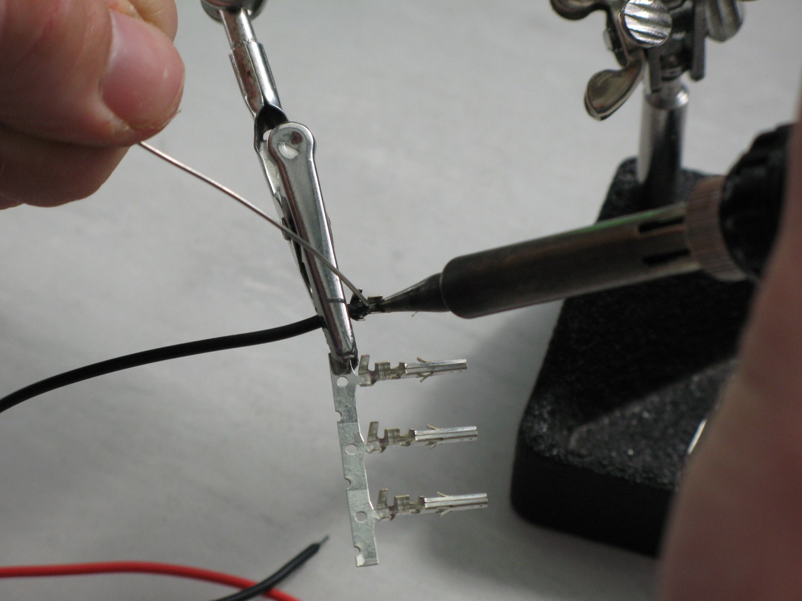
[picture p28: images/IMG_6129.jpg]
    
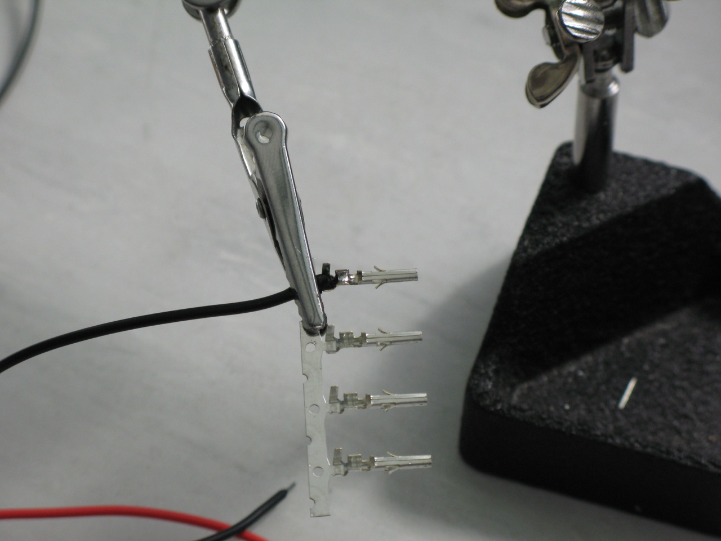
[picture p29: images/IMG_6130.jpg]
    

4. Remove the pin from the third hand clip (be careful it will be hot) and remove the unnecessary flap of metal at the base.

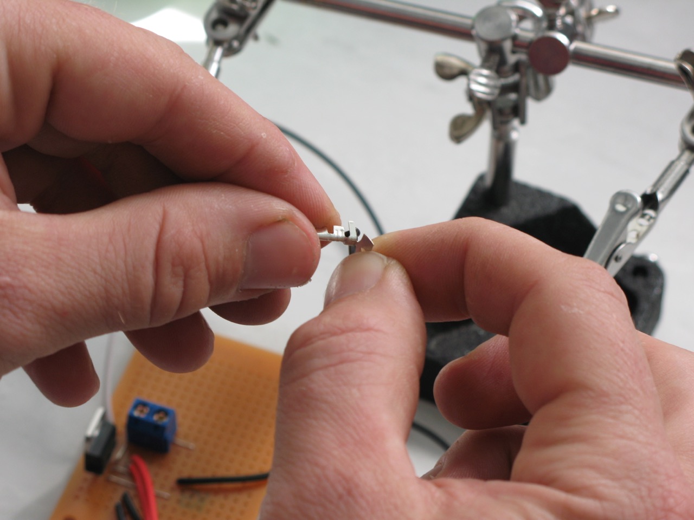
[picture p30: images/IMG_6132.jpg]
    

5. With the small needle-nose pliers fold the two flaps of metal inwards to hold the wire (alternatively crimp using a crimping tool).

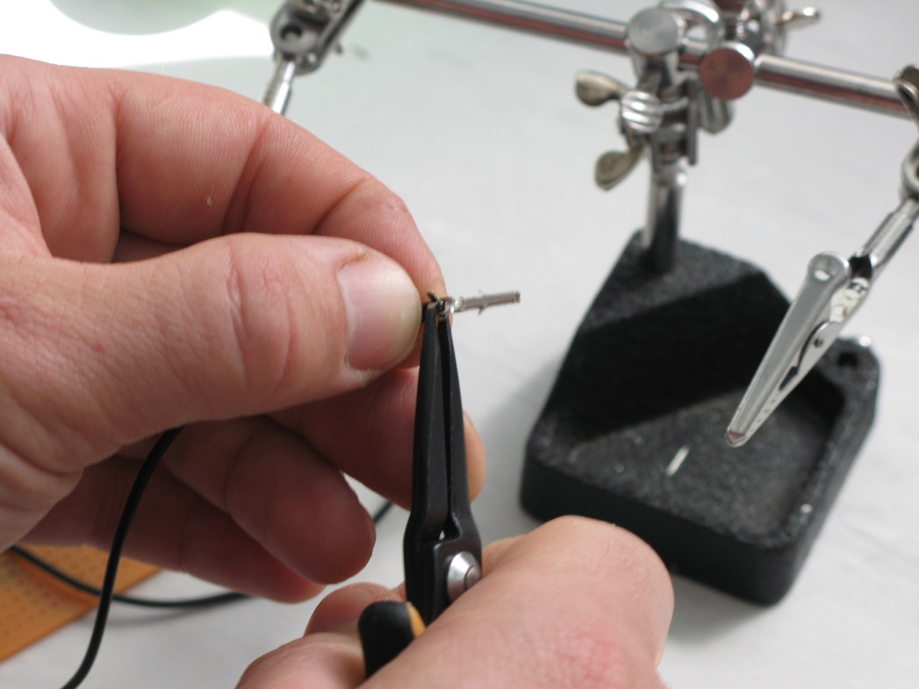
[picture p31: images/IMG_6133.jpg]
    
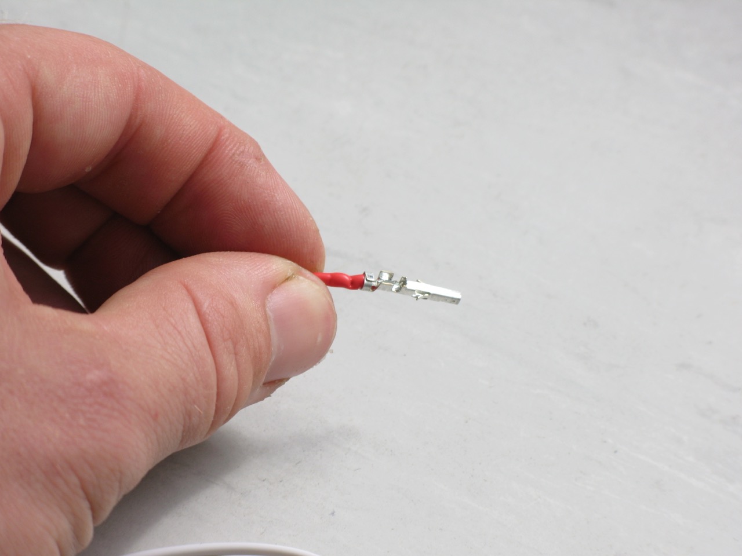
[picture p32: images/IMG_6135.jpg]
    

6. Repeat for the remaining wires and pins, but only for the male or female connector, whichever you chose. Keep the partner for later.

7. Insert the pins one at a time into the housing. These can only go in one way but might need a little extra push with the pliers to get them to clip all the way in. If they're not going in, possible causes might be:

    * Too much solder has been applied to the wire 
    * There is solder outside the channel where the wire sits
    * The wire is soldered too far in to pin
    * The pin is bent/deformed
    * The two little flaps on the side of the pin that clip into a groove in the housing and lock the pin in place have been damaged/deformed.

    It doesn't take much pin damage for it to be difficult/impossible to get these mini-molex pins into the housing. Unfortunately in most cases you just need to start again with a new set of connectors. The larger molex connectors are easier and have a more obvious 'click' when you insert the pin into the housing, but for the mini version you just need to ensure that the pin is all the way in and can't be pulled out when you try (but don't pull too hard!).

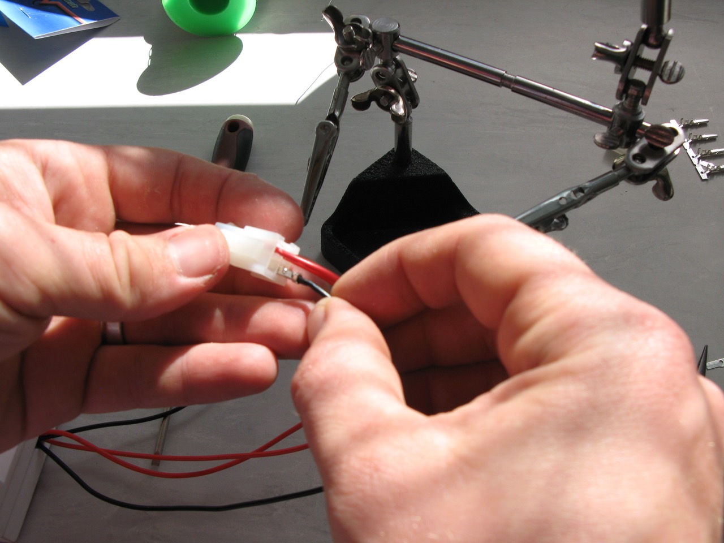
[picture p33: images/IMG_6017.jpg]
    

8. Done!

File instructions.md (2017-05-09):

This file has been replaced with separate instructions for each clamp version.

See the [README](./README.md) for more information.

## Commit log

2017-02-27 First version of instructions
    [Schematics.fzz]
2017-02-27 Minor update
    [Schematics.fzz]
2017-03-02 Links added to the new 3D printing resources repo. Updated the foot name.
2017-05-09 Clamp version 2 instructions added
2017-05-25 Instructions for lens lock assembly and fitting added
2017-05-26 Parts for lens locks added. Moved schematic to top.
2017-06-28 Added note about micro-adjusting the focus using some spongy material
2017-11-02 Added instructions for building the inline circuit
2018-07-09 Update version-2.md
    Typo. Specified achromatic hand lens instead of the aplanatic lens.
